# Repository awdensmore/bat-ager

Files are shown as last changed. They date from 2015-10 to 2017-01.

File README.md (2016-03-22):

# bat-ager

This project is an automated hardware and software tool for aging batteries in a precise fashion. The repo includes both hardware schematics and firmware.

**HARDWARE**

The aging process is done by repeatedly charging and discharging the battery. The hardware therefore switches between a charging mode and a discharging mode. Charging is done using a bi-directional DC/DC converter powered by a benchtop supply. Discharging is done via a DC/DC converter, carefully controlling a fet that shorts the battery to ground. Current is measured using a shunt and op-amp. The PCB is divided into five charging sections so that multiple batteries may be aged simultaneously. The system is controlled using an STM32F0 MCU. Also supports injecting a small AC ripple voltage during charging and discharging, which is used to measure the battery's impedance in real time.

**FIRMWARE**

The firmware is based on the STM HAL libraries. Features include: 
+ Independent charge/discharge settings for each battery
+ Constant current / constant voltage charging, low-voltage disconnect
+ Programmable load for discharging
+ Injection of small AC ripple voltage
+ Data collection and reporting

~~The firmware is Arduino based to make development easy (though I use the [Arduino makefile](https://github.com/sudar/Arduino-Makefile) to make customizing and automation easier in Linux). Features will include:~~
~~+ Independent charge/discharge settings for each battery~~
~~+ Serial communication via FTDI cable. With a Raspberry Pi attached, can be monitored via SSH.~~
~~+ Safeties ?!~~

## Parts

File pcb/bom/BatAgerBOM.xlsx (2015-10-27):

Bill of Materials
PCB: | Battery Ager |  |  |  | Per Unit Cost | ZAR 397.53
 |  |  |  |  | Quantity | 2
 |  |  |  |  | Components | ZAR 795.06
 |  |  |  |  | VAT @ 14% | ZAR 111.31
 |  |  |  |  | Total | ZAR 906.37
Reference | Type | Value | Package | Manufacturer | Part # | Price (ZAR) | Link | Notes
C1 | Cap | 47uF | PTH 11.2x6.3mm | Suntan | TS13D CD110X 47UF35V | 1.24 | http://www.mantech.co.za/ProductInfo.aspx?Item=72M3151
C10 | Cap | 0.1uF | 0805 | Yageo | C0805ZRY5V9BB104 | 0.28 | http://www.mantech.co.za/ProductInfo.aspx?Item=20M0861
C11 | Cap | 150uF | PTH 11.5x8mm | Rubycon | 35YXG150M 8x11.5 | 3 | http://www.mantech.co.za/ProductInfo.aspx?Item=72M4430
C12 | Cap | 150uF | PTH 11.5x8mm | Rubycon | 35YXG150M 8x11.5 | 3 | http://www.mantech.co.za/ProductInfo.aspx?Item=72M4431
C13 | Cap | 0.1uF | 0805 | Yageo | C0805ZRY5V9BB104 | 0.28 | http://www.mantech.co.za/ProductInfo.aspx?Item=20M0861
C14 | Cap | 0.1uF | 0805 | Yageo | C0805ZRY5V9BB104 | 0.28 | http://www.mantech.co.za/ProductInfo.aspx?Item=20M0861
C15 | Cap | 0.1uF | 0805 | Yageo | C0805ZRY5V9BB104 | 0.28 | http://www.mantech.co.za/ProductInfo.aspx?Item=20M0861
C16 | Cap | 0.1uF | 0805 | Yageo | C0805ZRY5V9BB104 | 0.28 | http://www.mantech.co.za/ProductInfo.aspx?Item=20M0861
C17 | Cap | 0.1uF | 0805 | Yageo | C0805ZRY5V9BB104 | 0.28 | http://www.mantech.co.za/ProductInfo.aspx?Item=20M0861
C18 | Cap | 0.1uF | 0805 | Yageo | C0805ZRY5V9BB104 | 0.28 | http://www.mantech.co.za/ProductInfo.aspx?Item=20M0861
C19 | Cap | 0.1uF | 0805 | Yageo | C0805ZRY5V9BB104 | 0.28 | http://www.mantech.co.za/ProductInfo.aspx?Item=20M0861
C2 | Cap | 47uF | PTH 11.2x6.3mm | Suntan | TS13D CD110X 47UF35V | 1.24 | http://www.mantech.co.za/ProductInfo.aspx?Item=72M3152
C20 | Cap | 0.1uF | 0805 | Yageo | C0805ZRY5V9BB104 | 0.28 | http://www.mantech.co.za/ProductInfo.aspx?Item=20M0861
C21 | Cap | 0.1uF | 0805 | Yageo | C0805ZRY5V9BB104 | 0.28 | http://www.mantech.co.za/ProductInfo.aspx?Item=20M0861
C22 | Cap | 0.1uF | 0805 | Yageo | C0805ZRY5V9BB104 | 0.28 | http://www.mantech.co.za/ProductInfo.aspx?Item=20M0861
C3 | Cap | 22pF | 0805 | Yageo | 0805CG221J500NT | 0.08 | http://www.mantech.co.za/ProductInfo.aspx?Item=35M3075
C4 | Cap | 0.1uF | 0805 | Yageo | C0805ZRY5V9BB104 | 0.28 | http://www.mantech.co.za/ProductInfo.aspx?Item=35M1227
C5 | Cap | 22pF | 0805 | Yageo | 0805CG221J500NT | 0.08 | http://www.mantech.co.za/ProductInfo.aspx?Item=35M3075
C6 | Cap | 22pF | 0805 | Yageo | 0805CG221J500NT | 0.08 | http://www.mantech.co.za/ProductInfo.aspx?Item=35M3075
C7 | Cap | 0.1uF | 0805 | Yageo | C0805ZRY5V9BB104 | 0.28 | http://www.mantech.co.za/ProductInfo.aspx?Item=20M0861
C8 | Cap | 0.1uF | 0805 | Yageo | C0805ZRY5V9BB104 | 0.28 | http://www.mantech.co.za/ProductInfo.aspx?Item=20M0861
C9 | Cap | 0.1uF | 0805 | Yageo | C0805ZRY5V9BB104 | 0.28 | http://www.mantech.co.za/ProductInfo.aspx?Item=20M0861
CON1 | Connector | ISP | PTH 2x3 100mil pitch |  |  |  |  | On hand
D1 | LED | Green | 0805 | Bright LED | BL-HX135A-TRB | 0.96 | http://www.mantech.co.za/ProductInfo.aspx?Item=12M0187
D10 | LED | Red | 0805 | Lite-On | LTST-C170EKT | 0.63 | http://www.mantech.co.za/ProductInfo.aspx?Item=35M5825
D2 | LED | Red | 0805 | Lite-On | LTST-C170EKT | 0.63 | http://www.mantech.co.za/ProductInfo.aspx?Item=35M5825
D3 | LED | Green | 0805 | Bright LED | BL-HX135A-TRB | 0.96 | http://www.mantech.co.za/ProductInfo.aspx?Item=12M0187
D4 | LED | Red | 0805 | Lite-On | LTST-C170EKT | 0.63 | http://www.mantech.co.za/ProductInfo.aspx?Item=35M5825
D5 | LED | Green | 0805 | Bright LED | BL-HX135A-TRB | 0.96 | http://www.mantech.co.za/ProductInfo.aspx?Item=12M0187
D6 | LED | Red | 0805 | Lite-On | LTST-C170EKT | 0.63 | http://www.mantech.co.za/ProductInfo.aspx?Item=35M5825
D7 | LED | Green | 0805 | Bright LED | BL-HX135A-TRB | 0.96 | http://www.mantech.co.za/ProductInfo.aspx?Item=12M0187
D8 | LED | Red | 0805 | Lite-On | LTST-C170EKT | 0.63 | http://www.mantech.co.za/ProductInfo.aspx?Item=35M5825
D9 | LED | Green | 0805 | Bright LED | BL-HX135A-TRB | 0.96 | http://www.mantech.co.za/ProductInfo.aspx?Item=12M0187
IC1 | MCU | 2560 | TQFP100 0.5mm pitch | Atmel | ATMEGA2560 | 270.97 | Farnell UK (http://export.farnell.com/webapp/wcs/stores/servlet/ProductDisplay?catalogId=15001&urlLangId=71&langId=71&productId=65349567&storeId=10152) | 11 pounds shipping from UK (phone estimate). Qty 4 sample on order directly from Atmel
P1 | Header | FTDI | PTH 1x6 100mil pitch |  |  |  |  | On hand
P10 | Header | BAT3 TERM | PTH 1x2 150mil pitch |  |  |  |  | On hand
P11 | Header | BAT4 TERM | PTH 1x2 150mil pitch |  |  |  |  | On hand
P12 | Header | BAT5 TERM | PTH 1x2 150mil pitch |  |  |  |  | On hand
P13 | Header | -15V | PTH 1 |  |  |  |  | On hand
P14 | Header | GND | PTH 1 |  |  |  |  | On hand
P15 | Header | AUX | PTH 1x6 100mil pitch |  |  |  |  | On hand
P16 | Header | Fan | PTH 1x2 150mil pitch |  |  |  |  | On hand
P2 | Header | +15V | PTH 1 |  |  |  |  | On hand
P3 | Header | BAT1 TP | PTH 1x5 100mil pitch |  |  |  |  | On hand
P4 | Header | BAT2 TP | PTH 1x5 100mil pitch |  |  |  |  | On hand
P5 | Header | BAT3 TP | PTH 1x5 100mil pitch |  |  |  |  | On hand
P6 | Header | BAT4 TP | PTH 1x5 100mil pitch |  |  |  |  | On hand
P7 | Header | BAT5 TP | PTH 1x5 100mil pitch |  |  |  |  | On hand
P8 | Header | BAT1 TERM | PTH 1x2 150mil pitch |  |  |  |  | On hand
P9 | Header | BAT2 TERM | PTH 1x2 150mil pitch |  |  |  |  | On hand
Q01 | T / FET | NFET | TO252 | IR | IRFR3607PBF | 9.78 | http://www.mantech.co.za/ProductInfo.aspx?Item=13M1648
Q02 | T / FET | Sgnl Trans | SOT23 | NXP | BC849B | 0.35 | http://www.mantech.co.za/ProductInfo.aspx?Item=35M3304
Q03 | T / FET | PFET | TO220 | IR | IRF9530N PBF | 7.05 | http://www.mantech.co.za/ProductInfo.aspx?Item=35M4416
Q04 | T / FET | NFET | TO220 | TI | CSD18536KCS | 0 | http://www.ti.com/product/csd18536kcs | On hand. Alternate part # AUIRL1404Z (IR) available from Farnell.
Q05 | T / FET | Sgnl Trans | SOT23 | NXP | BC849B | 0.35 | http://www.mantech.co.za/ProductInfo.aspx?Item=35M3304
Q06 | T / FET | Sgnl Trans | SOT23 | NXP | BC849B | 0.35 | http://www.mantech.co.za/ProductInfo.aspx?Item=35M3304
Q07 | T / FET | PFET | TO220 | IR | IRF9530N PBF | 7.05 | http://www.mantech.co.za/ProductInfo.aspx?Item=35M4416
Q08 | T / FET | NFET | TO220 | TI | CSD18536KCS | 0 | http://www.ti.com/product/csd18536kcs | On hand. Alternate part # AUIRL1404Z (IR) available from Farnell.
Q09 | T / FET | Sgnl Trans | SOT23 | NXP | BC849B | 0.35 | http://www.mantech.co.za/ProductInfo.aspx?Item=35M3304
Q10 | T / FET | Sgnl Trans | SOT23 | NXP | BC849B | 0.35 | http://www.mantech.co.za/ProductInfo.aspx?Item=35M3304
Q11 | T / FET | PFET | TO220 | IR | IRF9530N PBF | 7.05 | http://www.mantech.co.za/ProductInfo.aspx?Item=35M4416
Q12 | T / FET | Sgnl Trans | SOT23 | NXP | BC849B | 0.35 | http://www.mantech.co.za/ProductInfo.aspx?Item=35M3304
Q13 | T / FET | NFET | TO220 | TI | CSD18536KCS | 0 | http://www.ti.com/product/csd18536kcs | On hand. Alternate part # AUIRL1404Z (IR) available from Farnell.
Q14 | T / FET | Sgnl Trans | SOT23 | NXP | BC849B | 0.35 | http://www.mantech.co.za/ProductInfo.aspx?Item=35M3304
Q15 | T / FET | PFET | TO220 | IR | IRF9530N PBF | 7.05 | http://www.mantech.co.za/ProductInfo.aspx?Item=35M4416
Q16 | T / FET | Sgnl Trans | SOT23 | NXP | BC849B | 0.35 | http://www.mantech.co.za/ProductInfo.aspx?Item=35M3304
Q17 | T / FET | NFET | TO220 | TI | CSD18536KCS | 0 | http://www.ti.com/product/csd18536kcs | On hand. Alternate part # AUIRL1404Z (IR) available from Farnell.
Q18 | T / FET | Sgnl Trans | SOT23 | NXP | BC849B | 0.35 | http://www.mantech.co.za/ProductInfo.aspx?Item=35M3304
Q19 | T / FET | PFET | TO220 | IR | IRF9530N PBF | 7.05 | http://www.mantech.co.za/ProductInfo.aspx?Item=35M4416
Q20 | T / FET | Sgnl Trans | SOT23 | NXP | BC849B | 0.35 | http://www.mantech.co.za/ProductInfo.aspx?Item=35M3304
Q21 | T / FET | NFET | TO220 | TI | CSD18536KCS | 0 | http://www.ti.com/product/csd18536kcs | On hand. Alternate part # AUIRL1404Z (IR) available from Farnell.
Q22 | T / FET | NFET | TO220 | TI | IRFR3607PBF | 9.78 | http://www.mantech.co.za/ProductInfo.aspx?Item=13M1648
Q23 | T / FET | Sgnl Trans | SOT23 | NXP | BC849B | 0.35 | http://www.mantech.co.za/ProductInfo.aspx?Item=35M3304
Q24 | T / FET | Sgnl Trans | SOT23 | NXP | BC849B | 0.35 | http://www.mantech.co.za/ProductInfo.aspx?Item=35M3304
R1 | Resistor | 1k | 0805 | Yageo | RC0805JR-07 1K | 0.05 | http://www.mantech.co.za/ProductInfo.aspx?Item=35M1421
R10 | Resistor |  | PTH 10mm
R11 | Resistor |  | PTH 10mm
R12 | Resistor | 240 | 0805 | Yageo | RC0805FR-07 240R | 0.05 | http://www.mantech.co.za/ProductInfo.aspx?Item=35M3317
R13 | Resistor | 1k | 0805 | Yageo | RC0805JR-07 1K | 0.05 | http://www.mantech.co.za/ProductInfo.aspx?Item=35M1424
R14 | Resistor |  | PTH 10mm
R15 | Resistor | 1k | 0805 | Yageo | RC0805JR-07 1K | 0.05 | http://www.mantech.co.za/ProductInfo.aspx?Item=35M1425
R16 | Resistor | 1k | 0805 | Yageo | RC0805JR-07 1K | 0.05 | http://www.mantech.co.za/ProductInfo.aspx?Item=35M1426
R17 | Resistor | 240 | 0805 | Yageo | RC0805FR-07 240R | 0.05 | http://www.mantech.co.za/ProductInfo.aspx?Item=35M3317
R18 | Resistor | 240 | 0805 | Yageo | RC0805FR-07 240R | 0.05 | http://www.mantech.co.za/ProductInfo.aspx?Item=35M3317
R19 | Resistor | 0.056 | 2512 | Yageo | RL2512 FK-07 0R056 | 1.78 | http://www.mantech.co.za/ProductInfo.aspx?Item=20M0406
R2 | Resistor | 10k | 0805 | Yageo | RC0805JR-07 10K | 0.11 | http://www.mantech.co.za/ProductInfo.aspx?Item=35M1480
R20 | Resistor |  | PTH 10mm
R21 | Resistor |  | PTH 10mm
R22 | Resistor |  | PTH 10mm
R23 | Resistor |  | PTH 10mm
R24 | Resistor |  | PTH 10mm
R25 | Resistor |  | PTH 10mm
R26 | Resistor |  | PTH 10mm
R27 | Resistor | 240 | 0805 | Yageo | RC0805FR-07 240R | 0.05 | http://www.mantech.co.za/ProductInfo.aspx?Item=35M3317
R28 | Resistor | 1k | 0805 | Yageo | RC0805JR-07 1K | 0.05 | http://www.mantech.co.za/ProductInfo.aspx?Item=35M1427
R29 | Resistor |  | PTH 10mm
R3 | Resistor | 1M | 0805 | Yageo | RC0805JR-071M | 0.1 | http://www.mantech.co.za/ProductInfo.aspx?Item=35M3114
R30 | Resistor | 1k | 0805 | Yageo | RC0805JR-07 1K | 0.05 | http://www.mantech.co.za/ProductInfo.aspx?Item=35M1428
R31 | Resistor | 1k | 0805 | Yageo | RC0805JR-07 1K | 0.05 | http://www.mantech.co.za/ProductInfo.aspx?Item=35M1429
R32 | Resistor | 240 | 0805 | Yageo | RC0805FR-07 240R | 0.05 | http://www.mantech.co.za/ProductInfo.aspx?Item=35M3317
R33 | Resistor | 240 | 0805 | Yageo | RC0805FR-07 240R | 0.05 | http://www.mantech.co.za/ProductInfo.aspx?Item=35M3317
R34 | Resistor | 0.056 | 2512 | Yageo | RL2512 FK-07 0R056 | 1.78 | http://www.mantech.co.za/ProductInfo.aspx?Item=20M0406
R35 | Resistor |  | PTH 10mm
R36 | Resistor |  | PTH 10mm
R37 | Resistor |  | PTH 10mm
R38 | Resistor |  | PTH 10mm
R39 | Resistor |  | PTH 10mm
R4 | Resistor | 0 | 0805 | Yageo | RC0805JR-07 0R0 | 0.04 | http://www.mantech.co.za/ProductInfo.aspx?Item=20M0071
R40 | Resistor |  | PTH 10mm
R41 | Resistor |  | PTH 10mm
R42 | Resistor | 240 | 0805 | Yageo | RC0805FR-07 240R | 0.05 | http://www.mantech.co.za/ProductInfo.aspx?Item=35M3317
R43 | Resistor | 1k | 0805 | Yageo | RC0805JR-07 1K | 0.05 | http://www.mantech.co.za/ProductInfo.aspx?Item=35M1430
R44 | Resistor |  | PTH 10mm
R45 | Resistor | 1k | 0805 | Yageo | RC0805JR-07 1K | 0.05 | http://www.mantech.co.za/ProductInfo.aspx?Item=35M1431
R46 | Resistor | 1k | 0805 | Yageo | RC0805JR-07 1K | 0.05 | http://www.mantech.co.za/ProductInfo.aspx?Item=35M1432
R47 | Resistor | 240 | 0805 | Yageo | RC0805FR-07 240R | 0.05 | http://www.mantech.co.za/ProductInfo.aspx?Item=35M3317
R48 | Resistor | 240 | 0805 | Yageo | RC0805FR-07 240R | 0.05 | http://www.mantech.co.za/ProductInfo.aspx?Item=35M3317
R49 | Resistor | 0.056 | 2512 | Yageo | RL2512 FK-07 0R056 | 1.78 | http://www.mantech.co.za/ProductInfo.aspx?Item=20M0406
R5 | Resistor | 1k | 0805 | Yageo | RC0805JR-07 1K | 0.05 | http://www.mantech.co.za/ProductInfo.aspx?Item=35M1422
R50 | Resistor |  | PTH 10mm
R51 | Resistor |  | PTH 10mm
R52 | Resistor |  | PTH 10mm
R53 | Resistor |  | PTH 10mm
R54 | Resistor |  | PTH 10mm
R55 | Resistor |  | PTH 10mm
R56 | Resistor |  | PTH 10mm
R57 | Resistor | 240 | 0805 | Yageo | RC0805FR-07 240R | 0.05 | http://www.mantech.co.za/ProductInfo.aspx?Item=35M3317
R58 | Resistor | 1k | 0805 | Yageo | RC0805JR-07 1K | 0.05 | http://www.mantech.co.za/ProductInfo.aspx?Item=35M1433
R59 | Resistor |  | PTH 10mm
R6 | Resistor | 1k | 0805 | Yageo | RC0805JR-07 1K | 0.05 | http://www.mantech.co.za/ProductInfo.aspx?Item=35M1423
R60 | Resistor | 1k | 0805 | Yageo | RC0805JR-07 1K | 0.05 | http://www.mantech.co.za/ProductInfo.aspx?Item=35M1434
R61 | Resistor | 1k | 0805 | Yageo | RC0805JR-07 1K | 0.05 | http://www.mantech.co.za/ProductInfo.aspx?Item=35M1435
R62 | Resistor | 240 | 0805 | Yageo | RC0805FR-07 240R | 0.05 | http://www.mantech.co.za/ProductInfo.aspx?Item=35M3317
R63 | Resistor | 240 | 0805 | Yageo | RC0805FR-07 240R | 0.05 | http://www.mantech.co.za/ProductInfo.aspx?Item=35M3317
R64 | Resistor | 0.056 | 2512 | Yageo | RL2512 FK-07 0R056 | 1.78 | http://www.mantech.co.za/ProductInfo.aspx?Item=20M0406
R65 | Resistor |  | PTH 10mm
R66 | Resistor |  | PTH 10mm
R67 | Resistor |  | PTH 10mm
R68 | Resistor |  | PTH 10mm
R69 | Resistor |  | PTH 10mm
R7 | Resistor |  | PTH 10mm
R70 | Resistor |  | PTH 10mm
R71 | Resistor |  | PTH 10mm
R72 | Resistor | 240 | 0805 | Yageo | RC0805FR-07 240R | 0.05 | http://www.mantech.co.za/ProductInfo.aspx?Item=35M3317
R73 | Resistor | 1k | 0805 | Yageo | RC0805JR-07 1K | 0.05 | http://www.mantech.co.za/ProductInfo.aspx?Item=35M1436
R74 | Resistor |  | PTH 10mm
R75 | Resistor | 1k | 0805 | Yageo | RC0805JR-07 1K | 0.05 | http://www.mantech.co.za/ProductInfo.aspx?Item=35M1437
R76 | Resistor | 1k | 0805 | Yageo | RC0805JR-07 1K | 0.05 | http://www.mantech.co.za/ProductInfo.aspx?Item=35M1438
R77 | Resistor | 240 | 0805 | Yageo | RC0805FR-07 240R | 0.05 | http://www.mantech.co.za/ProductInfo.aspx?Item=35M3317
R78 | Resistor | 240 | 0805 | Yageo | RC0805FR-07 240R | 0.05 | http://www.mantech.co.za/ProductInfo.aspx?Item=35M3317
R79 | Resistor | 0.056 | 2512 | Yageo | RL2512 FK-07 0R056 | 1.78 | http://www.mantech.co.za/ProductInfo.aspx?Item=20M0406
R8 | Resistor |  | PTH 10mm
R80 | Resistor |  | PTH 10mm
R81 | Resistor |  | PTH 10mm
R82 | Resistor | 240 | 0805 | Yageo | RC0805FR-07 240R | 0.05 | http://www.mantech.co.za/ProductInfo.aspx?Item=35M3317
R83 | Resistor | 240 | 0805 | Yageo | RC0805FR-07 240R | 0.05 | http://www.mantech.co.za/ProductInfo.aspx?Item=35M3317
R84 | Resistor | 1k | 0805 | Yageo | RC0805JR-07 1K | 0.05 | http://www.mantech.co.za/ProductInfo.aspx?Item=35M1436
R9 | Resistor |  | PTH 10mm
SW1 | Switch |  | PTH 4pos | MEC | MTS-1102A TS-2 5MM | 2.97 | http://www.mantech.co.za/ProductInfo.aspx?Item=72M1360
U1 | IC | Op-amp | SOIC-8 | On-Semi | LM358DR2G DBK | 2.7 | http://www.mantech.co.za/ProductInfo.aspx?Item=72M1732
U2 | IC | Op-amp | SOIC-8 | On-Semi | LM358DR2G DBK | 3.7 | http://www.mantech.co.za/ProductInfo.aspx?Item=72M1733
U3 | IC | Op-amp | SOIC-8 | On-Semi | LM358DR2G DBK | 4.7 | http://www.mantech.co.za/ProductInfo.aspx?Item=72M1734
U4 | IC | Op-amp | SOIC-8 | On-Semi | LM358DR2G DBK | 5.7 | http://www.mantech.co.za/ProductInfo.aspx?Item=72M1735
U5 | IC | Op-amp | SOIC-8 | On-Semi | LM358DR2G DBK | 6.7 | http://www.mantech.co.za/ProductInfo.aspx?Item=72M1736
U6 | IC | Op-amp | SOIC-8 | On-Semi | LM358DR2G DBK | 7.7 | http://www.mantech.co.za/ProductInfo.aspx?Item=72M1737
Y1 | Crystal | 16MHz | HC49-USL | Mercury | 16.000MHZ-LP | 1.56 | http://www.mantech.co.za/ProductInfo.aspx?Item=65M1918-H
Other Mantech components
RJ45 |  |  |  |  | X98088S 8P8C MULTI | 7.68 | http://www.mantech.co.za/ProductInfo.aspx?Item=83M0020
14 pin DIP socket |  |  |  |  | ISS14T1/03/RH | 1.06 | http://www.mantech.co.za/ProductInfo.aspx?Item=70M0072 | MOQ: 34
8 pin DIP socket |  |  |  |  | ISS08T1/03 | 0.8 | http://www.mantech.co.za/ProductInfo.aspx?Item=70M0071 | MOQ: 60

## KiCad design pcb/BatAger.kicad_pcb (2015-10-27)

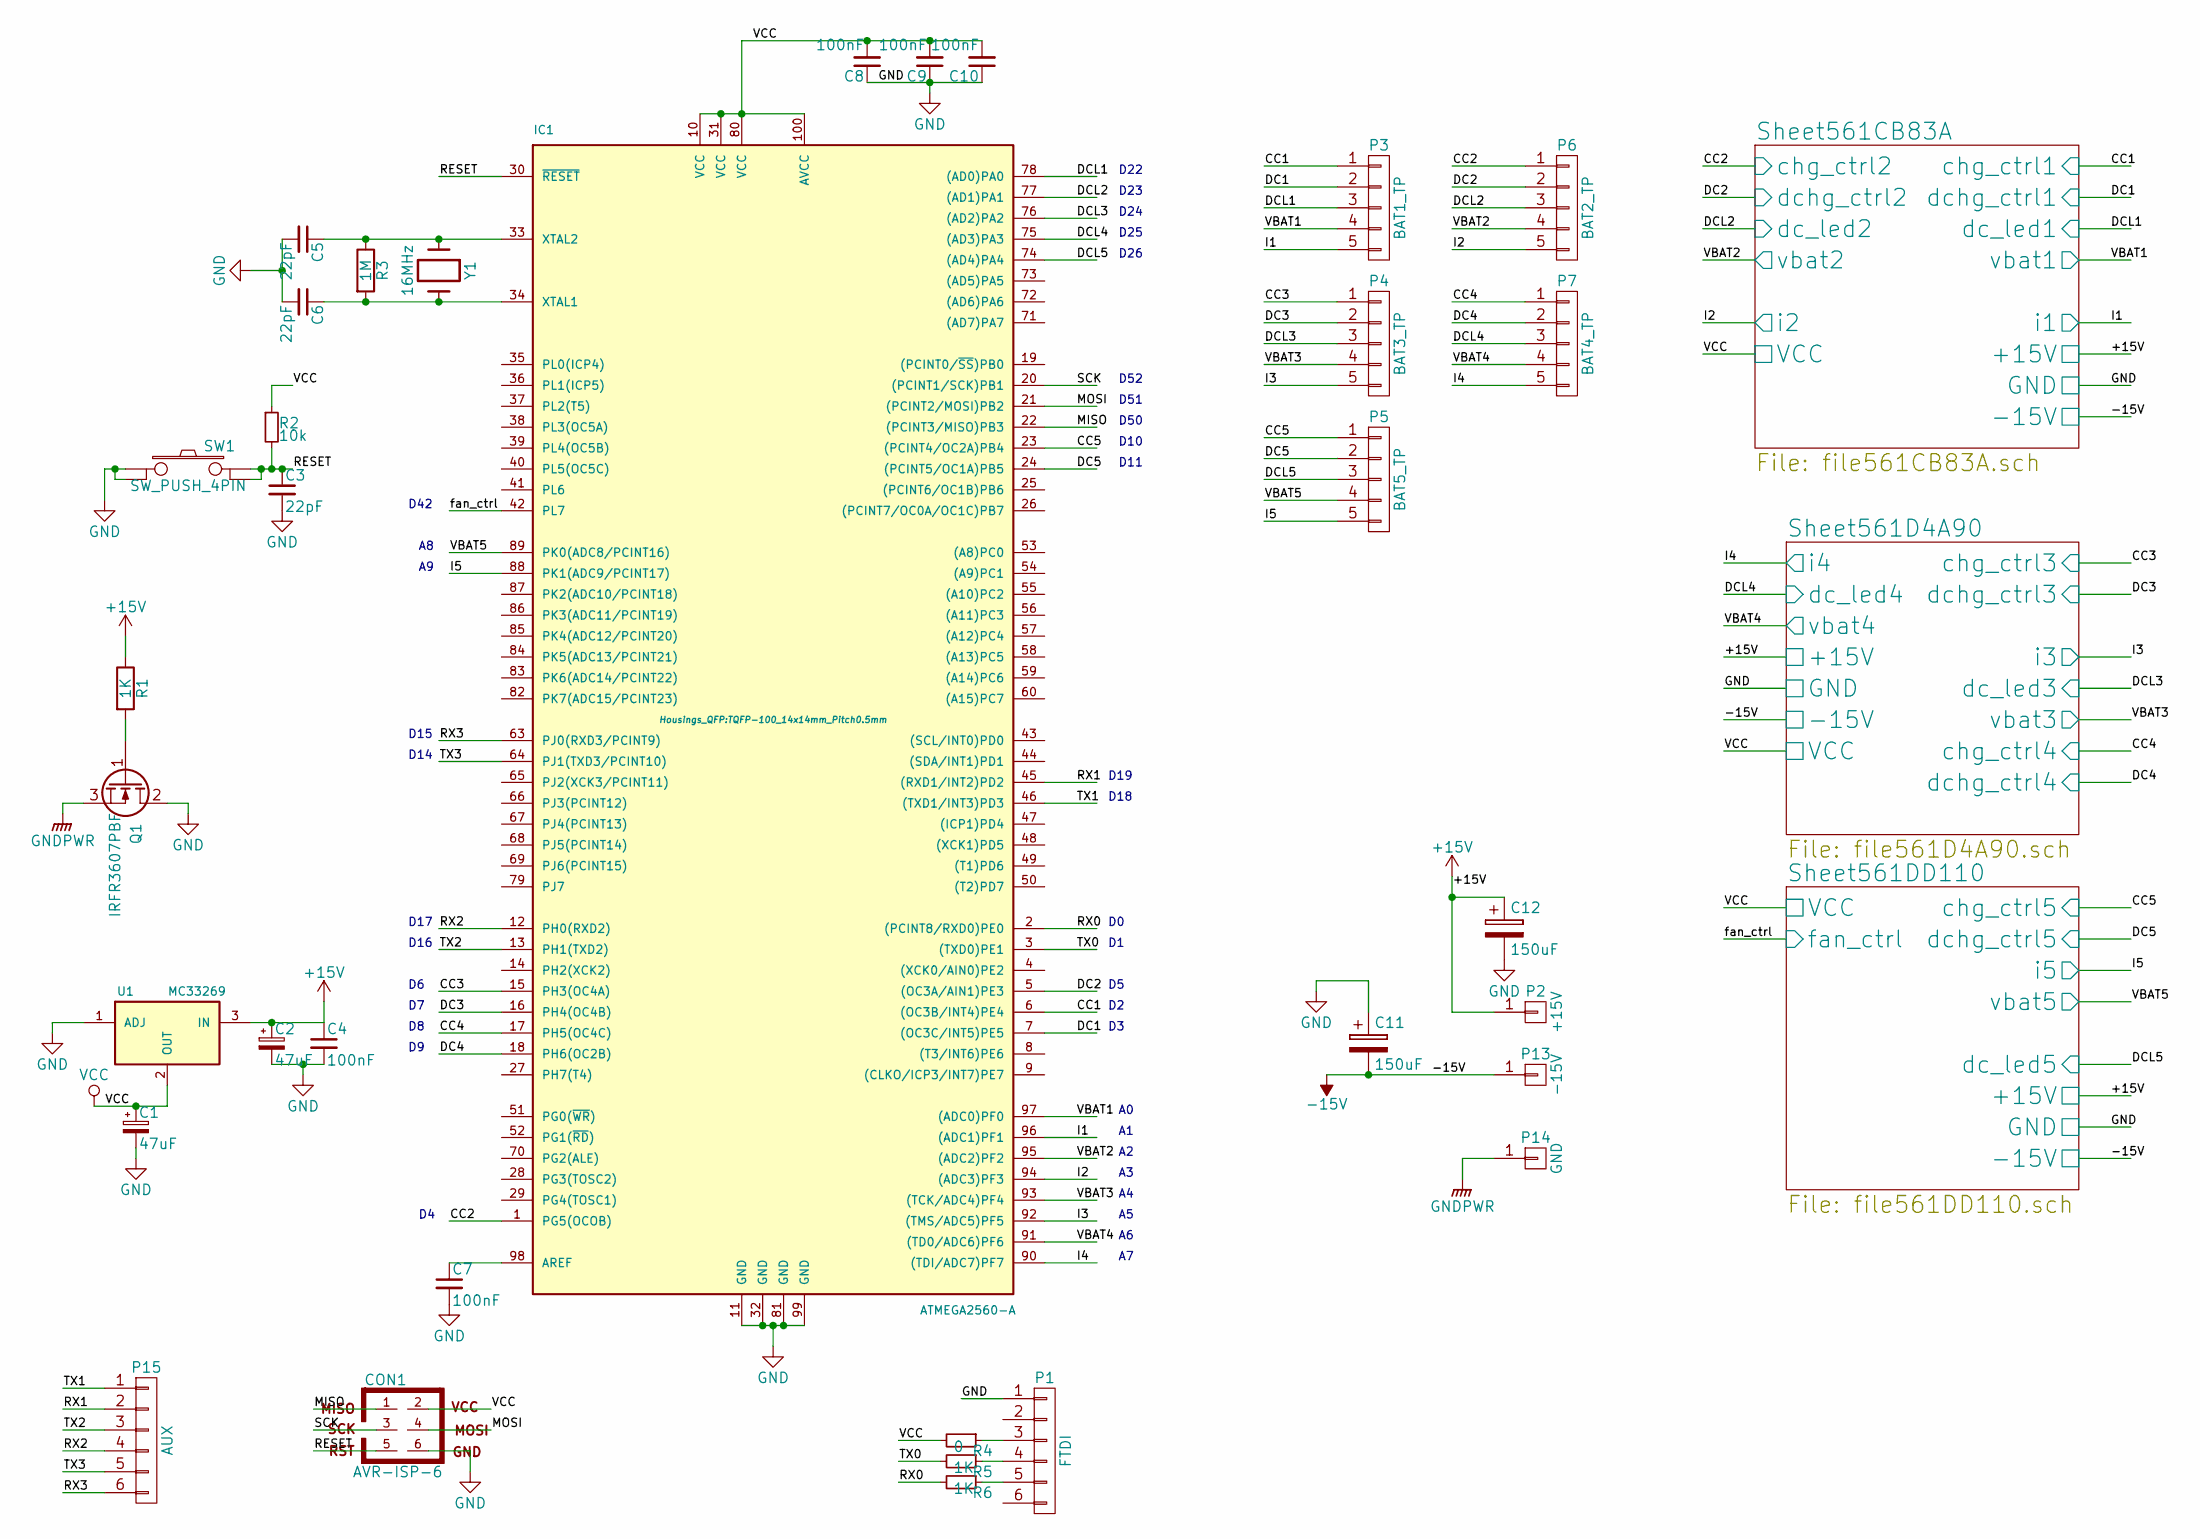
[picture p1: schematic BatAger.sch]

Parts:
C1, C2: 47uF; Elko_vert_11.2x6.3mm_RM2.5
C3, C5, C6: 22pF; C_0805_HandSoldering
C4, C7, C8, C9, C10: 100nF; C_0805_HandSoldering
C11, C12: 150uF; Elko_vert_11.5x8mm_RM3.5
CON1: AVR-ISP-6; Pin_Header_Straight_2x03
IC1: ATMEGA2560-A; TQFP-100_14x14mm_Pitch0.5mm
P1: FTDI; PINHEAD1-6
P2: +15V; Pin_Header_Straight_1x01
P3: BAT1_TP; Pin_Header_Straight_1x05
P4: BAT3_TP; Pin_Header_Straight_1x05
P5: BAT5_TP; Pin_Header_Straight_1x05
P6: BAT2_TP; Pin_Header_Straight_1x05
P7: BAT4_TP; Pin_Header_Straight_1x05
P13: -15V; Pin_Header_Straight_1x01
P14: GND; Pin_Header_Straight_1x01
P15: AUX; Pin_Header_Straight_1x06
Q1: IRFR3607PBF; TO-252-2Lead
R1, R5, R6: 1K; R_0805_HandSoldering
R2: 10k; R_0805_HandSoldering
R3: 1M; R_0805_HandSoldering
R4: 0; R_0805_HandSoldering
SW1: SW_PUSH_4PIN; SW_PUSH_4.5x6.5mm
U1: MC33269; TO-252-2Lead
Y1: 16MHz; Crystal_HC49-U_Vertical

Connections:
+15V: C2.1, C4.1, C12.1, P2.1, R1.1, U1.3 (IN); also elsewhere on the board
-15V: C11.2, P13.1; also elsewhere on the board
/MISO: CON1.1, IC1.22 ((PCINT3/MISO)PB3)
/MOSI: CON1.4, IC1.21 ((PCINT2/MOSI)PB2)
/RESET: C3.1, CON1.5, IC1.30 (~RESET), R2.2, SW1.2
/RX0: IC1.2 ((PCINT8/RXD0)PE0), R6.2
/RX1: IC1.45 ((RXD1/INT2)PD2), P15.2
/RX2: IC1.12 (PH0(RXD2)), P15.4
/RX3: IC1.63 (PJ0(RXD3/PCINT9)), P15.6
/SCK: CON1.3, IC1.20 ((PCINT1/SCK)PB1)
/Sheet561CB83A/chg_ctrl1: IC1.6 ((OC3B/INT4)PE4), P3.1; also elsewhere on the board
/Sheet561CB83A/chg_ctrl2: IC1.1 (PG5(OCOB)), P6.1; also elsewhere on the board
/Sheet561CB83A/dc_led1: IC1.78 ((AD0)PA0), P3.3; also elsewhere on the board
/Sheet561CB83A/dc_led2: IC1.77 ((AD1)PA1), P6.3; also elsewhere on the board
/Sheet561CB83A/dchg_ctrl1: IC1.7 ((OC3C/INT5)PE5), P3.2; also elsewhere on the board
/Sheet561CB83A/dchg_ctrl2: IC1.5 ((OC3A/AIN1)PE3), P6.2; also elsewhere on the board
/Sheet561CB83A/i1: IC1.96 ((ADC1)PF1), P3.5; also elsewhere on the board
/Sheet561CB83A/i2: IC1.94 ((ADC3)PF3), P6.5; also elsewhere on the board
/Sheet561CB83A/vbat1: IC1.97 ((ADC0)PF0), P3.4; also elsewhere on the board
/Sheet561CB83A/vbat2: IC1.95 ((ADC2)PF2), P6.4; also elsewhere on the board
/Sheet561D4A90/chg_ctrl3: IC1.15 (PH3(OC4A)), P4.1; also elsewhere on the board
/Sheet561D4A90/chg_ctrl4: IC1.17 (PH5(OC4C)), P7.1; also elsewhere on the board
/Sheet561D4A90/dc_led3: IC1.76 ((AD2)PA2), P4.3; also elsewhere on the board
/Sheet561D4A90/dc_led4: IC1.75 ((AD3)PA3), P7.3; also elsewhere on the board
/Sheet561D4A90/dchg_ctrl3: IC1.16 (PH4(OC4B)), P4.2; also elsewhere on the board
/Sheet561D4A90/dchg_ctrl4: IC1.18 (PH6(OC2B)), P7.2; also elsewhere on the board
/Sheet561D4A90/i3: IC1.92 ((TMS/ADC5)PF5), P4.5; also elsewhere on the board
/Sheet561D4A90/i4: IC1.90 ((TDI/ADC7)PF7), P7.5; also elsewhere on the board
/Sheet561D4A90/vbat3: IC1.93 ((TCK/ADC4)PF4), P4.4; also elsewhere on the board
/Sheet561D4A90/vbat4: IC1.91 ((TD0/ADC6)PF6), P7.4; also elsewhere on the board
/Sheet561DD110/chg_ctrl5: IC1.23 ((PCINT4/OC2A)PB4), P5.1; also elsewhere on the board
/Sheet561DD110/dc_led5: IC1.74 ((AD4)PA4), P5.3; also elsewhere on the board
/Sheet561DD110/dchg_ctrl5: IC1.24 ((PCINT5/OC1A)PB5), P5.2; also elsewhere on the board
/Sheet561DD110/fan_ctrl: IC1.42 (PL7); also elsewhere on the board
/Sheet561DD110/i5: IC1.88 (PK1(ADC9/PCINT17)), P5.5; also elsewhere on the board
/Sheet561DD110/vbat5: IC1.89 (PK0(ADC8/PCINT16)), P5.4; also elsewhere on the board
/TX0: IC1.3 ((TXD0)PE1), R5.2
/TX1: IC1.46 ((TXD1/INT3)PD3), P15.1
/TX2: IC1.13 (PH1(TXD2)), P15.3
/TX3: IC1.64 (PJ1(TXD3/PCINT10)), P15.5
GND: C1.2, C2.2, C3.2, C4.2, C5.2, C6.2, C7.2, C8.1, C9.1, C10.1, C11.1, C12.2, CON1.6, IC1.11 (GND), IC1.32 (GND), IC1.81 (GND), IC1.99 (GND), P1.1, Q1.2 (D), SW1.1, U1.1 (ADJ); also elsewhere on the board
GNDPWR: P14.1, Q1.3 (S)
unnamed: C5.1, IC1.33 (XTAL2), R3.1, Y1.1
unnamed: C6.1, IC1.34 (XTAL1), R3.2, Y1.2
unnamed: C7.1, IC1.98 (AREF)
unnamed: P1.3, R4.1
unnamed: P1.4, R5.1
unnamed: P1.5, R6.1
unnamed: Q1.1 (G), R1.2
VCC: C1.1, C8.2, C9.2, C10.2, CON1.2, IC1.10 (VCC), IC1.31 (VCC), IC1.80 (VCC), IC1.100 (AVCC), R2.1, R4.2, U1.2 (OUT); also elsewhere on the board

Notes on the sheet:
D22
D23
D24
D25
D10
D11
D26
D50
D51
D52
D18
D19
D16
D17
D14
D15
D42

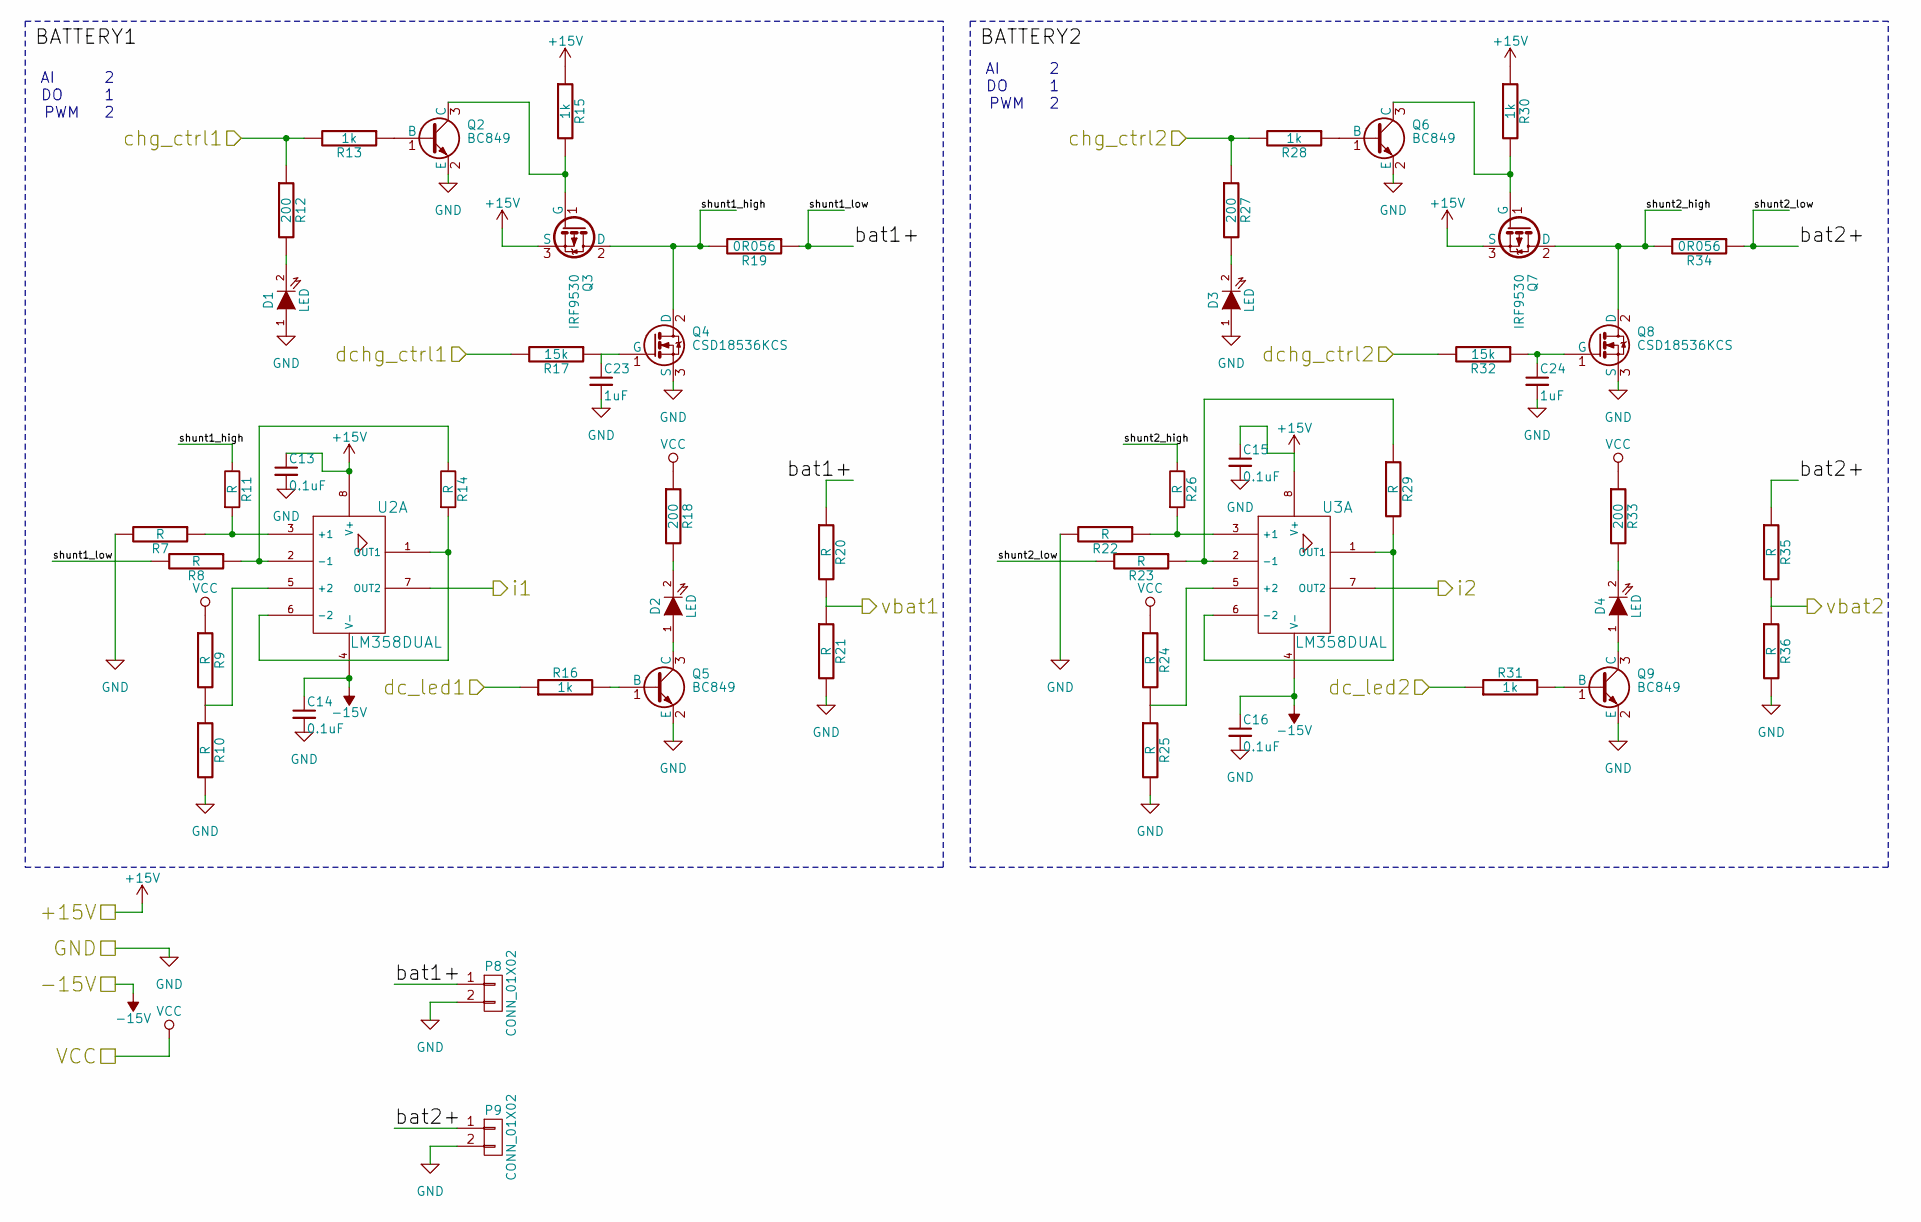
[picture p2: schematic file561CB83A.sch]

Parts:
C13, C14, C15, C16: 0.1uF; C_0805_HandSoldering
C23, C24: 1uF; C_0805_HandSoldering
D1, D2, D3, D4: LED; LED-0805
P8, P9: CONN_01X02; PINHEAD1-2_200mil
Q2, Q5, Q6, Q9: BC849; SOT-23_Handsoldering
Q3, Q7: IRF9530; TO-220
Q4, Q8: CSD18536KCS; TO-220
R7, R8, R9, R10, R11, R14, R20, R21, R22, R23, R24, R25, R26, R29, R35, R36: R; Resistor_Horizontal_RM10mm
R12, R18: 200; R_0805_HandSoldering; Part # RC0805JR-07 200R
R13, R16: 1k; R_0805_HandSoldering; Part # RC0805JR-07 200R
R15, R28, R30, R31: 1k; R_0805_HandSoldering
R17: 15k; R_0805_HandSoldering; Part # RC0805JR-07 200R
R19, R34: 0R056; R_2512_HandSoldering
R27, R33: 200; R_0805_HandSoldering
R32: 15k; R_0805_HandSoldering
U2, U3: LM358DUAL; SOIC-8_3.9x4.9mm_Pitch1.27mm

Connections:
+15V: C13.1, C15.1, Q3.3 (S), Q7.3 (S), R15.1, R30.1, U2.8 (V+), U3.8 (V+); also elsewhere on the board
-15V: C14.1, C16.1, U2.4 (V-), U3.4 (V-); also elsewhere on the board
/Sheet561CB83A/bat1+: P8.1, R8.2, R19.1, R20.1
/Sheet561CB83A/bat2+: P9.1, R23.2, R34.1, R35.1
/Sheet561CB83A/chg_ctrl1: R12.1, R13.2; also elsewhere on the board
/Sheet561CB83A/chg_ctrl2: R27.1, R28.2; also elsewhere on the board
/Sheet561CB83A/dc_led1: R16.1; also elsewhere on the board
/Sheet561CB83A/dc_led2: R31.1; also elsewhere on the board
/Sheet561CB83A/dchg_ctrl1: R17.2; also elsewhere on the board
/Sheet561CB83A/dchg_ctrl2: R32.2; also elsewhere on the board
/Sheet561CB83A/i1: U2.7 (OUT2); also elsewhere on the board
/Sheet561CB83A/i2: U3.7 (OUT2); also elsewhere on the board
/Sheet561CB83A/shunt1_high: Q3.2 (D), Q4.2 (D), R11.1, R19.2
/Sheet561CB83A/shunt2_high: Q7.2 (D), Q8.2 (D), R26.1, R34.2
/Sheet561CB83A/vbat1: R20.2, R21.1; also elsewhere on the board
/Sheet561CB83A/vbat2: R35.2, R36.1; also elsewhere on the board
GND: C13.2, C14.2, C15.2, C16.2, C23.2, C24.2, D1.1 (A), D3.1 (A), P8.2, P9.2, Q2.2 (E), Q4.3 (S), Q5.2 (E), Q6.2 (E), Q8.3 (S), Q9.2 (E), R7.2, R10.2, R21.2, R22.2, R25.2, R36.2; also elsewhere on the board
unnamed: C23.1, Q4.1 (G), R17.1
unnamed: C24.1, Q8.1 (G), R32.1
unnamed: D1.2 (K), R12.2
unnamed: D2.1 (A), Q5.3 (C)
unnamed: D2.2 (K), R18.2
unnamed: D3.2 (K), R27.2
unnamed: D4.1 (A), Q9.3 (C)
unnamed: D4.2 (K), R33.2
unnamed: Q2.1 (B), R13.1
unnamed: Q2.3 (C), Q3.1 (G), R15.2
unnamed: Q5.1 (B), R16.2
unnamed: Q6.1 (B), R28.1
unnamed: Q6.3 (C), Q7.1 (G), R30.2
unnamed: Q9.1 (B), R31.2
unnamed: R9.2, R10.1, U2.5 (+2)
unnamed: R7.1, R11.2, U2.3 (+1)
unnamed: R8.1, R14.1, U2.2 (-1)
unnamed: R14.2, U2.1 (OUT1), U2.6 (-2)
unnamed: R22.1, R26.2, U3.3 (+1)
unnamed: R23.1, R29.1, U3.2 (-1)
unnamed: R24.2, R25.1, U3.5 (+2)
unnamed: R29.2, U3.1 (OUT1), U3.6 (-2)
VCC: R9.1, R18.1, R24.1, R33.1; also elsewhere on the board

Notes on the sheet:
AI 2 DO 1 PWM 2

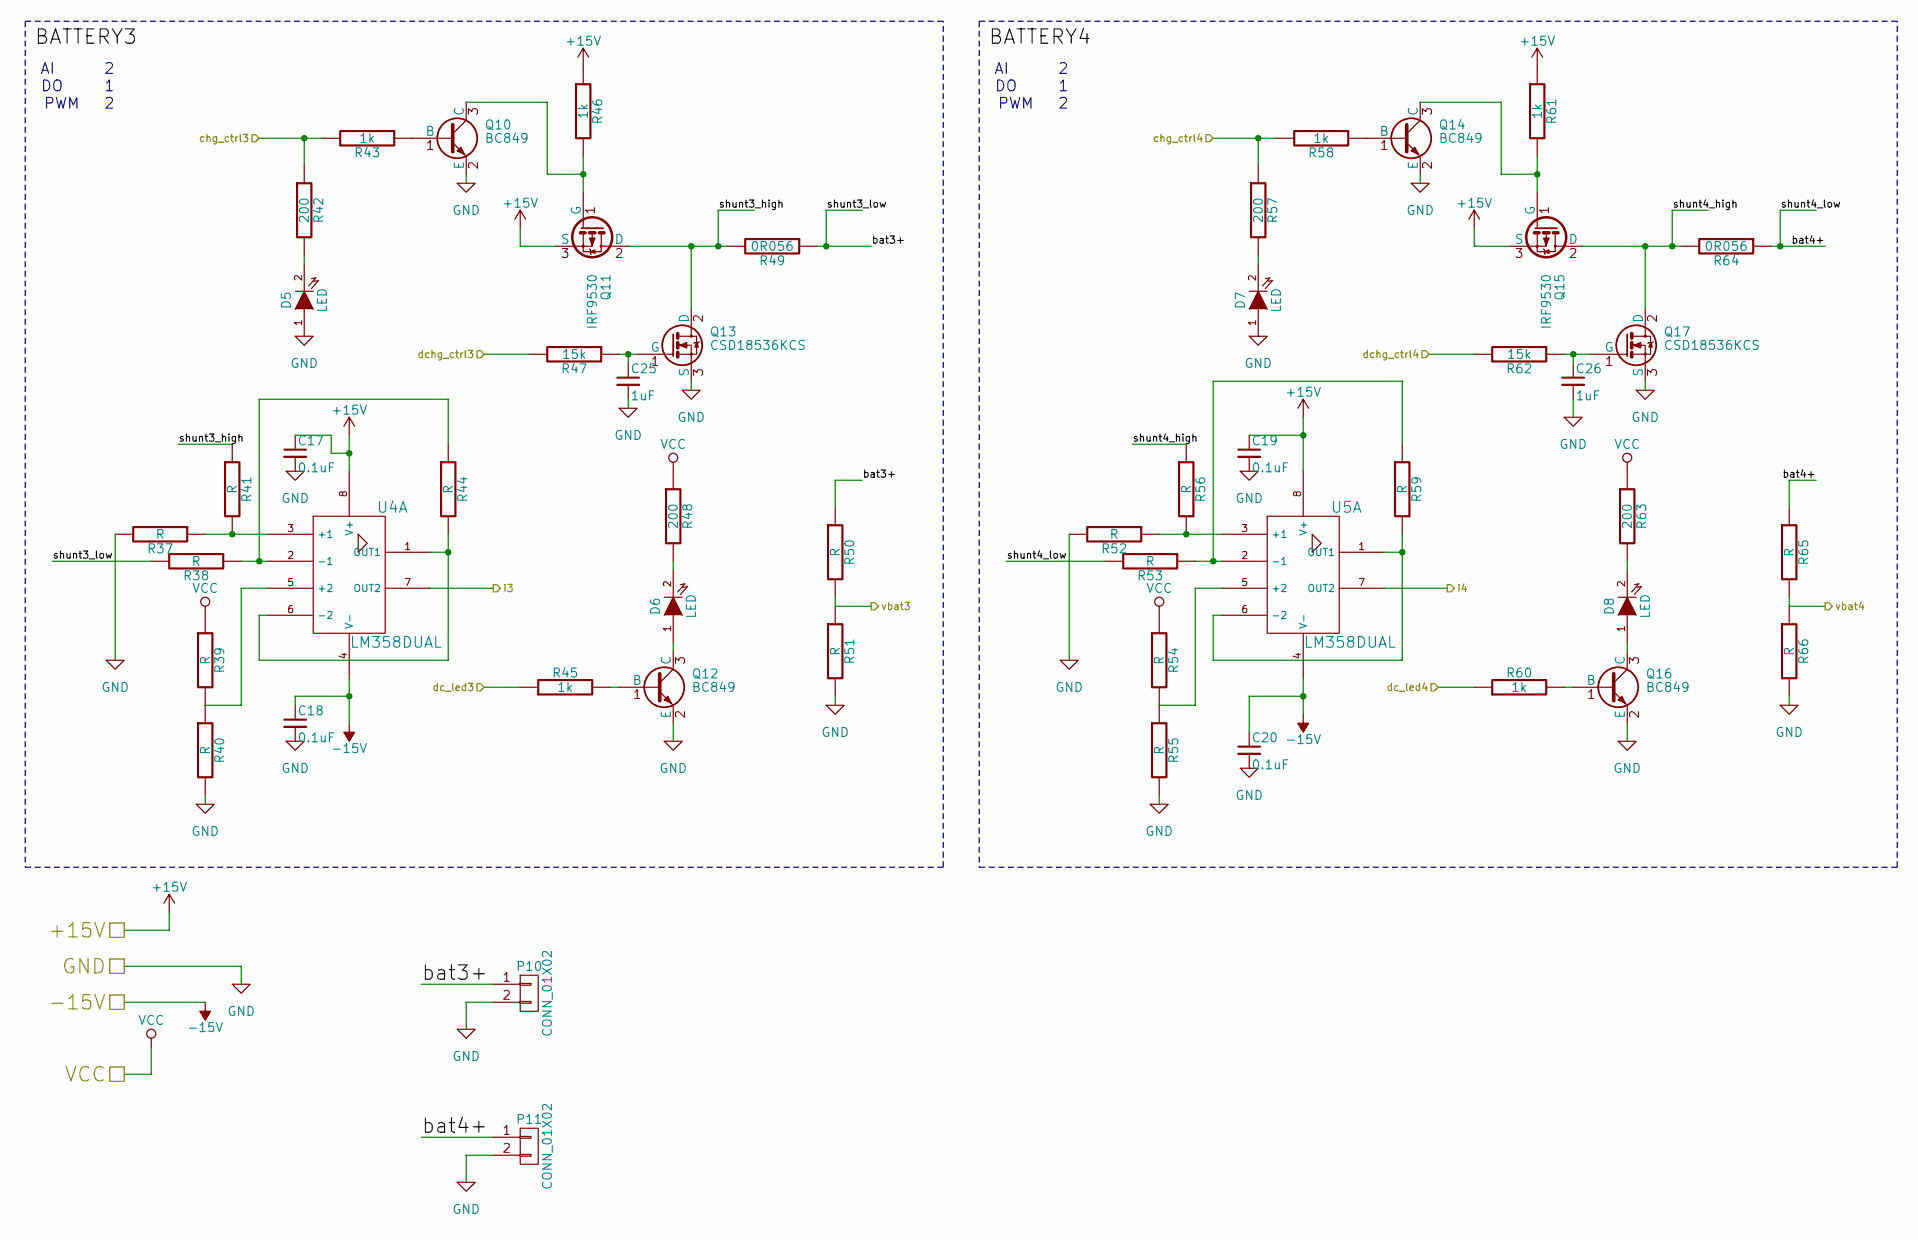
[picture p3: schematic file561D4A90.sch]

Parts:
C17, C18, C19, C20: 0.1uF; C_0805_HandSoldering
C25: 1uF; C_0805_HandSoldering
C26: 1uF; C_Disc_D3_P2.5
D5, D6, D7, D8: LED; LED-0805
P10, P11: CONN_01X02; PINHEAD1-2_200mil
Q10, Q12, Q14, Q16: BC849; SOT-23_Handsoldering
Q11, Q15: IRF9530; TO-220
Q13, Q17: CSD18536KCS; TO-220
R37, R38, R39, R40, R41, R44, R50, R51, R52, R53, R54, R55, R56, R59, R65, R66: R; Resistor_Horizontal_RM10mm
R42, R48, R57, R63: 200; R_0805_HandSoldering
R43, R45, R46, R58, R60, R61: 1k; R_0805_HandSoldering
R47: 15k; R_0805_HandSoldering
R49, R64: 0R056; R_2512_HandSoldering; Part # RL2512 FK-07 0R056
R62: 15k; Resistor_Horizontal_RM10mm
U4, U5: LM358DUAL; SOIC-8_3.9x4.9mm_Pitch1.27mm

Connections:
+15V: C17.1, C19.1, Q11.3 (S), Q15.3 (S), R46.1, R61.1, U4.8 (V+), U5.8 (V+); also elsewhere on the board
-15V: C18.1, C20.1, U4.4 (V-), U5.4 (V-); also elsewhere on the board
/Sheet561D4A90/bat3+: P10.1, R38.2, R49.1, R50.1
/Sheet561D4A90/bat4+: P11.1, R53.2, R64.1, R65.1
/Sheet561D4A90/chg_ctrl3: R42.1, R43.2; also elsewhere on the board
/Sheet561D4A90/chg_ctrl4: R57.1, R58.2; also elsewhere on the board
/Sheet561D4A90/dc_led3: R45.1; also elsewhere on the board
/Sheet561D4A90/dc_led4: R60.1; also elsewhere on the board
/Sheet561D4A90/dchg_ctrl3: R47.2; also elsewhere on the board
/Sheet561D4A90/dchg_ctrl4: R62.2; also elsewhere on the board
/Sheet561D4A90/i3: U4.7 (OUT2); also elsewhere on the board
/Sheet561D4A90/i4: U5.7 (OUT2); also elsewhere on the board
/Sheet561D4A90/shunt3_high: Q11.2 (D), Q13.2 (D), R41.1, R49.2
/Sheet561D4A90/shunt4_high: Q15.2 (D), Q17.2 (D), R56.1, R64.2
/Sheet561D4A90/vbat3: R50.2, R51.1; also elsewhere on the board
/Sheet561D4A90/vbat4: R65.2, R66.1; also elsewhere on the board
GND: C17.2, C18.2, C19.2, C20.2, C25.2, C26.2, D5.1 (A), D7.1 (A), P10.2, P11.2, Q10.2 (E), Q12.2 (E), Q13.3 (S), Q14.2 (E), Q16.2 (E), Q17.3 (S), R37.2, R40.2, R51.2, R52.2, R55.2, R66.2; also elsewhere on the board
unnamed: C25.1, Q13.1 (G), R47.1
unnamed: C26.1, Q17.1 (G), R62.1
unnamed: D5.2 (K), R42.2
unnamed: D6.1 (A), Q12.3 (C)
unnamed: D6.2 (K), R48.2
unnamed: D7.2 (K), R57.2
unnamed: D8.1 (A), Q16.3 (C)
unnamed: D8.2 (K), R63.2
unnamed: Q10.1 (B), R43.1
unnamed: Q10.3 (C), Q11.1 (G), R46.2
unnamed: Q12.1 (B), R45.2
unnamed: Q14.1 (B), R58.1
unnamed: Q14.3 (C), Q15.1 (G), R61.2
unnamed: Q16.1 (B), R60.2
unnamed: R37.1, R41.2, U4.3 (+1)
unnamed: R38.1, R44.1, U4.2 (-1)
unnamed: R39.2, R40.1, U4.5 (+2)
unnamed: R44.2, U4.1 (OUT1), U4.6 (-2)
unnamed: R52.1, R56.2, U5.3 (+1)
unnamed: R53.1, R59.1, U5.2 (-1)
unnamed: R54.2, R55.1, U5.5 (+2)
unnamed: R59.2, U5.1 (OUT1), U5.6 (-2)
VCC: R39.1, R48.1, R54.1, R63.1; also elsewhere on the board

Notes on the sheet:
AI 2 DO 1 PWM 2

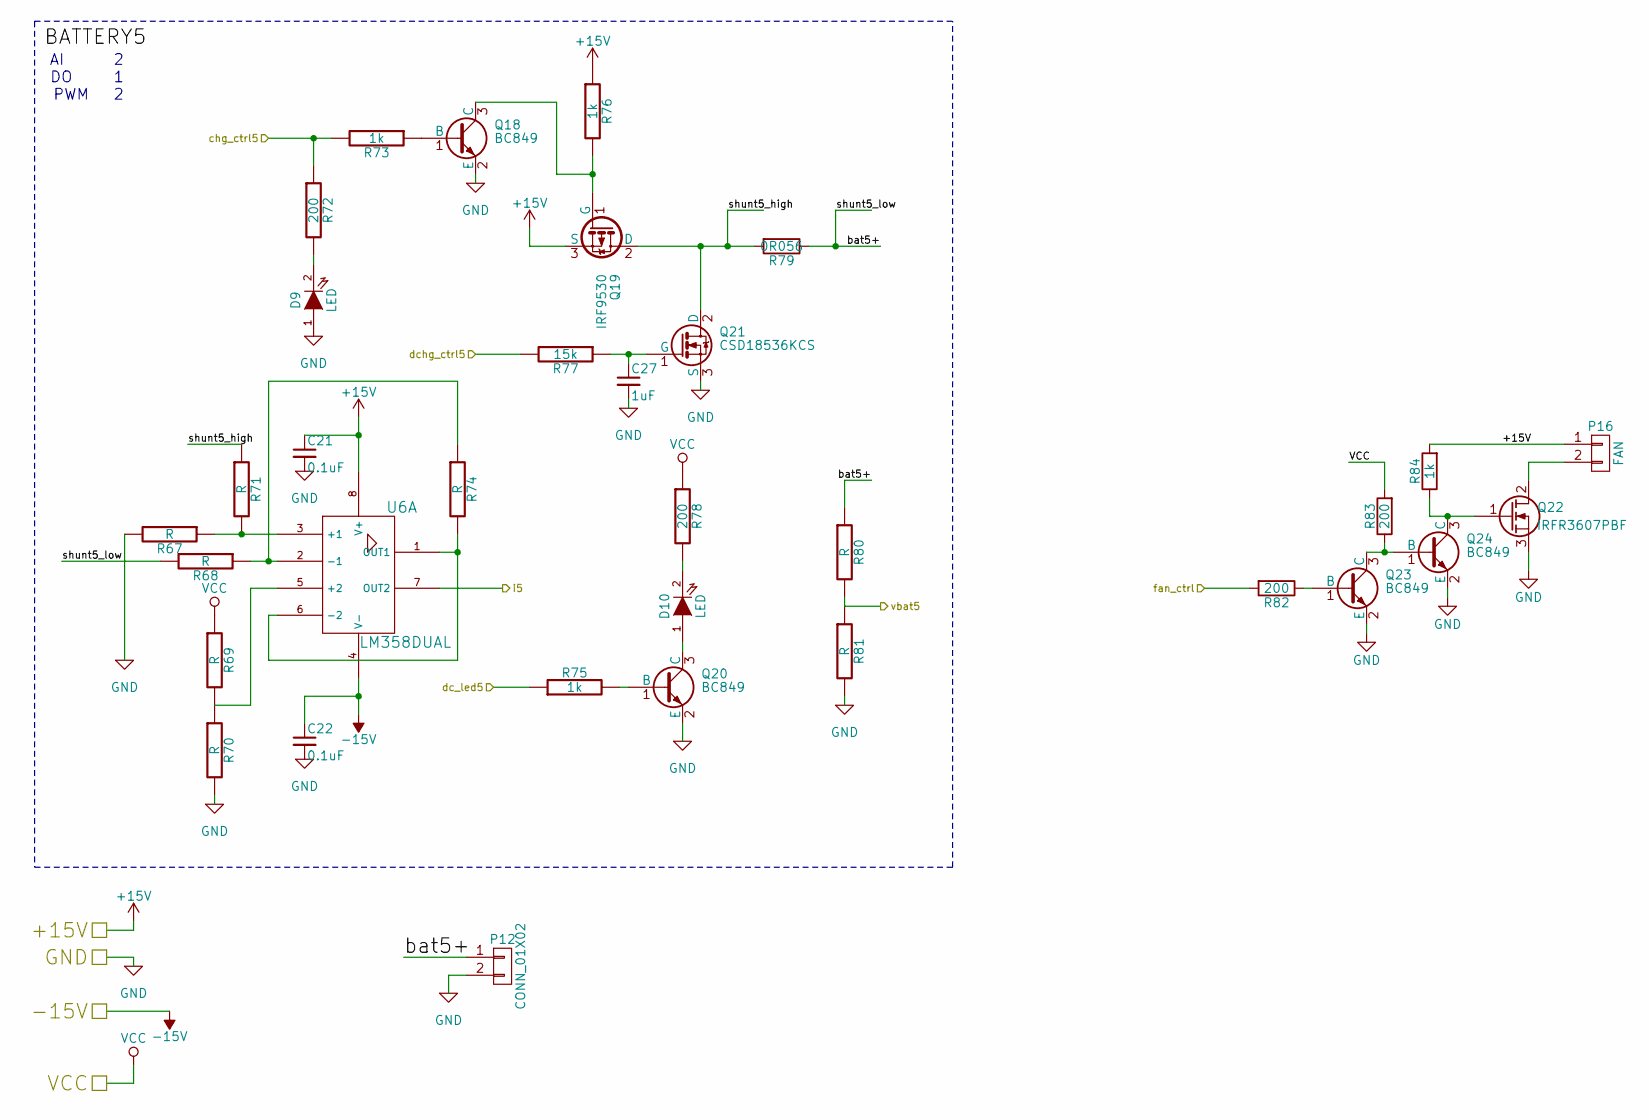
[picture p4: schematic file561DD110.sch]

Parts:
C21, C22: 0.1uF; C_0805_HandSoldering
C27: 1uF; C_0805_HandSoldering
D9, D10: LED; LED-0805
P12: CONN_01X02; PINHEAD1-2_200mil
P16: FAN; Pin_Header_Straight_1x02
Q18, Q20, Q23, Q24: BC849; SOT-23_Handsoldering
Q19: IRF9530; TO-220
Q21: CSD18536KCS; TO-220
Q22: IRFR3607PBF; TO-252-2Lead
R67, R68, R69, R70, R71, R74, R80, R81: R; Resistor_Horizontal_RM10mm
R72, R78, R82, R83: 200; R_0805_HandSoldering
R73, R75, R76, R84: 1k; R_0805_HandSoldering
R77: 15k; R_0805_HandSoldering
R79: 0R056; R_2512_HandSoldering; Part # RL2512 FK-07 0R056
U6: LM358DUAL; SOIC-8_3.9x4.9mm_Pitch1.27mm

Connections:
+15V: C21.1, P16.1, Q19.3 (S), R76.1, R84.2, U6.8 (V+); also elsewhere on the board
-15V: C22.1, U6.4 (V-); also elsewhere on the board
/Sheet561DD110/bat5+: P12.1, R68.2, R79.1, R80.1
/Sheet561DD110/chg_ctrl5: R72.1, R73.2; also elsewhere on the board
/Sheet561DD110/dc_led5: R75.1; also elsewhere on the board
/Sheet561DD110/dchg_ctrl5: R77.2; also elsewhere on the board
/Sheet561DD110/fan_ctrl: R82.2; also elsewhere on the board
/Sheet561DD110/i5: U6.7 (OUT2); also elsewhere on the board
/Sheet561DD110/shunt5_high: Q19.2 (D), Q21.2 (D), R71.1, R79.2
/Sheet561DD110/vbat5: R80.2, R81.1; also elsewhere on the board
GND: C21.2, C22.2, C27.2, D9.1 (A), P12.2, Q18.2 (E), Q20.2 (E), Q21.3 (S), Q22.3 (S), Q23.2 (E), Q24.2 (E), R67.2, R70.2, R81.2; also elsewhere on the board
unnamed: C27.1, Q21.1 (G), R77.1
unnamed: D9.2 (K), R72.2
unnamed: D10.1 (A), Q20.3 (C)
unnamed: D10.2 (K), R78.2
unnamed: P16.2, Q22.2 (D)
unnamed: Q18.1 (B), R73.1
unnamed: Q18.3 (C), Q19.1 (G), R76.2
unnamed: Q20.1 (B), R75.2
unnamed: Q22.1 (G), Q24.3 (C), R84.1
unnamed: Q23.1 (B), R82.1
unnamed: Q23.3 (C), Q24.1 (B), R83.1
unnamed: R67.1, R71.2, U6.3 (+1)
unnamed: R68.1, R74.1, U6.2 (-1)
unnamed: R69.2, R70.1, U6.5 (+2)
unnamed: R74.2, U6.1 (OUT1), U6.6 (-2)
VCC: R69.1, R78.1, R83.2; also elsewhere on the board

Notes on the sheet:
AI 2 DO 1 PWM 2

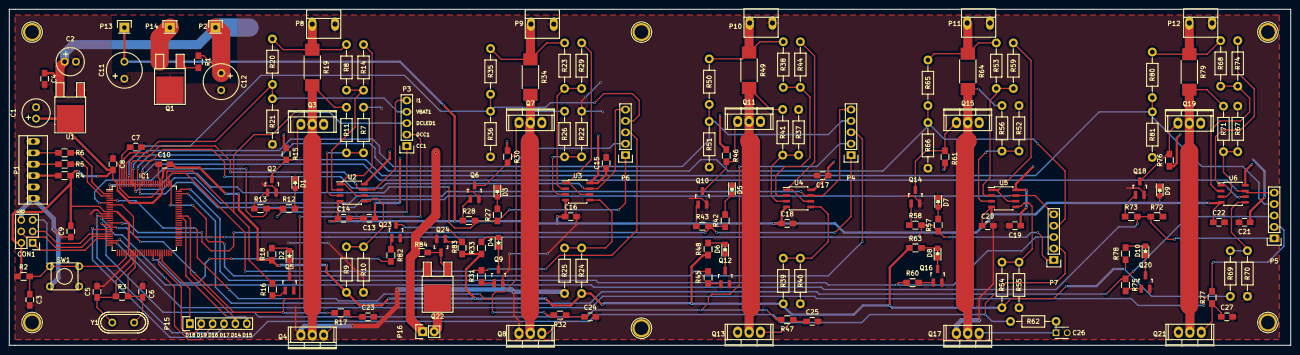
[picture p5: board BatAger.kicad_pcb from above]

Board: 2 copper layers, 285.8 x 74.9 mm, 171 parts (0 on the bottom side), 119 nets.

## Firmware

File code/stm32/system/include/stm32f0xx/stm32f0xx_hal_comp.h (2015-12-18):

/**
  ******************************************************************************
  * @file    stm32f0xx_hal_comp.h
  * @author  MCD Application Team
  * @version V1.3.0
  * @date    26-June-2015
  * @brief   Header file of COMP HAL module.
  ******************************************************************************
  * @attention
  *
  * <h2><center>&copy; COPYRIGHT(c) 2015 STMicroelectronics</center></h2>
  *
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
  ******************************************************************************  
  */

/* Define to prevent recursive inclusion -------------------------------------*/
#ifndef __STM32F0xx_HAL_COMP_H
#define __STM32F0xx_HAL_COMP_H

#ifdef __cplusplus
 extern "C" {
#endif

#if defined(STM32F051x8) || defined(STM32F058xx) || \
    defined(STM32F071xB) || defined(STM32F072xB) || defined(STM32F078xx) || \
    defined(STM32F091xC) || defined(STM32F098xx)

/* Includes ------------------------------------------------------------------*/
#include "stm32f0xx_hal_def.h"

/** @addtogroup STM32F0xx_HAL_Driver
  * @{
  */

/** @addtogroup COMP COMP
  * @{
  */ 

/* Exported types ------------------------------------------------------------*/ 
/** @defgroup COMP_Exported_Types COMP Exported Types
  * @{
  */
    
/** 
  * @brief  COMP Init structure definition  
  */ 
typedef struct
{

  uint32_t InvertingInput;     /*!< Selects the inverting input of the comparator.
                                    This parameter can be a value of @ref COMP_InvertingInput */

  uint32_t NonInvertingInput;  /*!< Selects the non inverting input of the comparator.
                                    This parameter can be a value of @ref COMP_NonInvertingInput */

  uint32_t Output;             /*!< Selects the output redirection of the comparator.
                                    This parameter can be a value of @ref COMP_Output */

  uint32_t OutputPol;          /*!< Selects the output polarity of the comparator.
                                    This parameter can be a value of @ref COMP_OutputPolarity */

  uint32_t Hysteresis;         /*!< Selects the hysteresis voltage of the comparator.
                                    This parameter can be a value of @ref COMP_Hysteresis */

  uint32_t Mode;               /*!< Selects the operating comsumption mode of the comparator
                                    to adjust the speed/consumption.
                                    This parameter can be a value of @ref COMP_Mode */

  uint32_t WindowMode;         /*!< Selects the window mode of the comparator 1 & 2.
                                    This parameter can be a value of @ref COMP_WindowMode */
  
  uint32_t TriggerMode;        /*!< Selects the trigger mode of the comparator (interrupt mode).
                                    This parameter can be a value of @ref COMP_TriggerMode */

}COMP_InitTypeDef;

/** 
  * @brief  COMP Handle Structure definition  
  */ 
typedef struct
{
  COMP_TypeDef                *Instance; /*!< Register base address    */
  COMP_InitTypeDef            Init;      /*!< COMP required parameters */
  HAL_LockTypeDef             Lock;      /*!< Locking object           */
  __IO uint32_t               State;     /*!< COMP communication state 
                                              This parameter can be a value of @ref COMP_State  */
}COMP_HandleTypeDef;

/**
  * @}
  */
  
/* Exported constants --------------------------------------------------------*/
/** @defgroup COMP_Exported_Constants COMP Exported Constants
  * @{
  */

/** @defgroup COMP_State COMP State
  * @{
  */
#define HAL_COMP_STATE_RESET             ((uint32_t)0x00000000)    /*!< COMP not yet initialized or disabled             */
#define HAL_COMP_STATE_READY             ((uint32_t)0x00000001)    /*!< COMP initialized and ready for use               */
#define HAL_COMP_STATE_READY_LOCKED      ((uint32_t)0x00000011)    /*!< COMP initialized but the configuration is locked */
#define HAL_COMP_STATE_BUSY              ((uint32_t)0x00000002)    /*!< COMP is running                                  */
#define HAL_COMP_STATE_BUSY_LOCKED       ((uint32_t)0x00000012)    /*!< COMP is running and the configuration is locked  */
/**
  * @}
  */

/** @defgroup COMP_OutputPolarity COMP OutputPolarity
  * @{
  */
#define COMP_OUTPUTPOL_NONINVERTED             ((uint32_t)0x00000000)  /*!< COMP output on GPIO isn't inverted */
#define COMP_OUTPUTPOL_INVERTED                COMP_CSR_COMP1POL       /*!< COMP output on GPIO is inverted  */
/**
  * @}
  */ 

/** @defgroup COMP_Hysteresis COMP Hysteresis
  * @{
  */
#define COMP_HYSTERESIS_NONE                   ((uint32_t)0x00000000)  /*!< No hysteresis */
#define COMP_HYSTERESIS_LOW                    COMP_CSR_COMP1HYST_0    /*!< Hysteresis level low */
#define COMP_HYSTERESIS_MEDIUM                 COMP_CSR_COMP1HYST_1    /*!< Hysteresis level medium */
#define COMP_HYSTERESIS_HIGH                   COMP_CSR_COMP1HYST      /*!< Hysteresis level high */
/**
  * @}
  */

/** @defgroup COMP_Mode COMP Mode
  * @{
  */
/* Please refer to the electrical characteristics in the device datasheet for
   the power consumption values */
#define COMP_MODE_HIGHSPEED                    ((uint32_t)0x00000000) /*!< High Speed */
#define COMP_MODE_MEDIUMSPEED                  COMP_CSR_COMP1MODE_0   /*!< Medium Speed */
#define COMP_MODE_LOWPOWER                     COMP_CSR_COMP1MODE_1   /*!< Low power mode */
#define COMP_MODE_ULTRALOWPOWER                COMP_CSR_COMP1MODE     /*!< Ultra-low power mode */
/**
  * @}
  */

/** @defgroup COMP_InvertingInput COMP InvertingInput
  * @{
  */

#define COMP_INVERTINGINPUT_1_4VREFINT         ((uint32_t)0x00000000) /*!< 1/4 VREFINT connected to comparator inverting input */
#define COMP_INVERTINGINPUT_1_2VREFINT         COMP_CSR_COMP1INSEL_0                         /*!< 1/2 VREFINT connected to comparator inverting input    */
#define COMP_INVERTINGINPUT_3_4VREFINT         COMP_CSR_COMP1INSEL_1                         /*!< 3/4 VREFINT connected to comparator inverting input    */
#define COMP_INVERTINGINPUT_VREFINT            (COMP_CSR_COMP1INSEL_1|COMP_CSR_COMP1INSEL_0) /*!< VREFINT connected to comparator inverting input        */
#define COMP_INVERTINGINPUT_DAC1               COMP_CSR_COMP1INSEL_2                         /*!< DAC_OUT1 (PA4) connected to comparator inverting input */
#define COMP_INVERTINGINPUT_DAC1SWITCHCLOSED   (COMP_CSR_COMP1INSEL_2|COMP_CSR_COMP1SW1)     /*!< DAC_OUT1 (PA4) connected to comparator inverting input 
                                                                                                  and close switch (PA0 for COMP1 only) */
#define COMP_INVERTINGINPUT_DAC2               (COMP_CSR_COMP1INSEL_2|COMP_CSR_COMP1INSEL_0) /*!< DAC_OUT2 (PA5) connected to comparator inverting input */
#define COMP_INVERTINGINPUT_IO1                (COMP_CSR_COMP1INSEL_2|COMP_CSR_COMP1INSEL_1) /*!< IO (PA0 for COMP1 and PA2 for COMP2) connected to comparator inverting input */
/**
  * @}
  */ 

/** @defgroup COMP_NonInvertingInput COMP NonInvertingInput
  * @{
  */
#define COMP_NONINVERTINGINPUT_IO1               ((uint32_t)0x00000000) /*!< I/O1 (PA1 for COMP1, PA3 for COMP2) 
                                                                             connected to comparator non inverting input */
#define COMP_NONINVERTINGINPUT_DAC1SWITCHCLOSED  COMP_CSR_COMP1SW1  /*!< DAC ouput connected to comparator COMP1 non inverting input */
/**
  * @}
  */

/** @defgroup COMP_Output COMP Output
  * @{
  */

/* Output Redirection common for COMP1 and COMP2 */
#define COMP_OUTPUT_NONE                       ((uint32_t)0x00000000)                          /*!< COMP output isn't connected to other peripherals */
#define COMP_OUTPUT_TIM1BKIN                   COMP_CSR_COMP1OUTSEL_0                          /*!< COMP output connected to TIM1 Break Input (BKIN) */
#define COMP_OUTPUT_TIM1IC1                    COMP_CSR_COMP1OUTSEL_1                          /*!< COMP output connected to TIM1 Input Capture 1 */
#define COMP_OUTPUT_TIM1OCREFCLR               (COMP_CSR_COMP1OUTSEL_1|COMP_CSR_COMP1OUTSEL_0) /*!< COMP output connected to TIM1 OCREF Clear */
#define COMP_OUTPUT_TIM2IC4                    COMP_CSR_COMP1OUTSEL_2                          /*!< COMP output connected to TIM2 Input Capture 4 */
#define COMP_OUTPUT_TIM2OCREFCLR               (COMP_CSR_COMP1OUTSEL_2|COMP_CSR_COMP1OUTSEL_0) /*!< COMP output connected to TIM2 OCREF Clear */
#define COMP_OUTPUT_TIM3IC1                    (COMP_CSR_COMP1OUTSEL_2|COMP_CSR_COMP1OUTSEL_1) /*!< COMP output connected to TIM3 Input Capture 1 */
#define COMP_OUTPUT_TIM3OCREFCLR               COMP_CSR_COMP1OUTSEL                            /*!< COMP output connected to TIM3 OCREF Clear */
/**
  * @}
  */ 

/** @defgroup COMP_OutputLevel COMP OutputLevel
  * @{
  */ 
/* When output polarity is not inverted, comparator output is low when
   the non-inverting input is at a lower voltage than the inverting input*/
#define COMP_OUTPUTLEVEL_LOW                   ((uint32_t)0x00000000)
/* When output polarity is not inverted, comparator output is high when
   the non-inverting input is at a higher voltage than the inverting input */
#define COMP_OUTPUTLEVEL_HIGH                  COMP_CSR_COMP1OUT
/**
  * @}
  */ 

/** @defgroup COMP_TriggerMode COMP TriggerMode
  * @{
  */
#define COMP_TRIGGERMODE_NONE                  ((uint32_t)0x00000000)  /*!< No External Interrupt trigger detection */
#define COMP_TRIGGERMODE_IT_RISING             ((uint32_t)0x00000001)  /*!< External Interrupt Mode with Rising edge trigger detection */
#define COMP_TRIGGERMODE_IT_FALLING            ((uint32_t)0x00000002)  /*!< External Interrupt Mode with Falling edge trigger detection */
#define COMP_TRIGGERMODE_IT_RISING_FALLING     ((uint32_t)0x00000003)  /*!< External Interrupt Mode with Rising/Falling edge trigger detection */
#define COMP_TRIGGERMODE_EVENT_RISING          ((uint32_t)0x00000010)  /*!< Event Mode with Rising edge trigger detection */
#define COMP_TRIGGERMODE_EVENT_FALLING         ((uint32_t)0x00000020)  /*!< Event Mode with Falling edge trigger detection */
#define COMP_TRIGGERMODE_EVENT_RISING_FALLING  ((uint32_t)0x00000030)  /*!< Event Mode with Rising/Falling edge trigger detection */
/**
  * @}
  */ 

/** @defgroup COMP_WindowMode COMP WindowMode
  * @{
  */
#define COMP_WINDOWMODE_DISABLE                ((uint32_t)0x00000000)  /*!< Window mode disabled */
#define COMP_WINDOWMODE_ENABLE                 COMP_CSR_WNDWEN         /*!< Window mode enabled: non inverting input of comparator 2
                                                                            is connected to the non inverting input of comparator 1 (PA1) */
/**
  * @}
  */

/** @defgroup COMP_Flag COMP Flag
  * @{
  */
#define COMP_FLAG_LOCK                         ((uint32_t)COMP_CSR_COMPxLOCK)  /*!< Lock flag */

/**
  * @}
  */

/**
  * @}
  */ 
  
/* Exported macros -----------------------------------------------------------*/
/** @defgroup COMP_Exported_Macros COMP Exported Macros
  * @{
  */

/** @brief  Reset COMP handle state
  * @param  __HANDLE__: COMP handle.
  * @retval None
  */
#define __HAL_COMP_RESET_HANDLE_STATE(__HANDLE__) ((__HANDLE__)->State = HAL_COMP_STATE_RESET)

/**
  * @brief  Enable the specified comparator.
  * @param  __HANDLE__: COMP handle.
  * @retval None
  */
#define __HAL_COMP_ENABLE(__HANDLE__)                 (((__HANDLE__)->Instance == COMP1) ?    \
                                                       SET_BIT(COMP->CSR, COMP_CSR_COMP1EN) : \
                                                       SET_BIT(COMP->CSR, COMP_CSR_COMP2EN))
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

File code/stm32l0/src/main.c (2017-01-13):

/**
  ******************************************************************************
  * File Name          : main.c
  * Description        : Main program body
  ******************************************************************************
*/
/* Includes ------------------------------------------------------------------*/
#include "stm32l0xx_hal.h"
#include "user_funcs.h"

/* Private variables ---------------------------------------------------------*/
ADC_HandleTypeDef hadc;

TIM_HandleTypeDef htim2;
TIM_HandleTypeDef htim22;
DMA_HandleTypeDef hdma_tim2_ch1;
DMA_HandleTypeDef hdma_tim2_ch2;
DMA_HandleTypeDef hdma_tim2_ch3;
DMA_HandleTypeDef hdma_tim2_ch4;

/* Private variables ---------------------------------------------------------*/

/* Private function prototypes -----------------------------------------------*/
void SystemClock_Config(void);
static void MX_GPIO_Init(void);
static void MX_DMA_Init(void);
static void MX_ADC_Init(void);
static void MX_TIM2_Init(void);
static void MX_TIM22_Init(void);
void conv_init(batpins batx);

int main(void)
{

  /* MCU Configuration----------------------------------------------------------*/

  /* Reset of all peripherals, Initializes the Flash interface and the Systick. */
  HAL_Init();

  /* Configure the system clock */
  SystemClock_Config();

  /* Initialize all configured peripherals */
  MX_GPIO_Init();
  MX_DMA_Init();
  MX_ADC_Init();
  MX_TIM2_Init();
  MX_TIM22_Init();

  batpins battery3;
  batpins battery4;
  pwm_timers b3_tims;
  pwm_timers b4_tims;
  batprops props_bat3;
  batprops props_bat4;

  /* Battery 3 */
  b3_tims.conv_timer = htim2;
  b3_tims.dchg_timer = htim22;

  battery3.v_adc_chan = ADC_CHANNEL_4;
  battery3.i_adc_chan = ADC_CHANNEL_8;
  battery3.chg_port = chg_onoff_3_GPIO_Port;
  battery3.chg_pin = chg_onoff_3_Pin;
  battery3.dchg_pin = TIM_CHANNEL_1;
  battery3.conv_chg_pin = TIM_CHANNEL_1;
  battery3.conv_dchg_pin = TIM_CHANNEL_2;
  battery3.pwm_tims = b3_tims;

  props_bat3.i_adc_val = 0;
  props_bat3.v_adc_val = 0;
  props_bat3.adc_val_old = adc_read(battery3.i_adc_chan);
  props_bat3.id_adc_stpt = 993 + props_bat3.adc_val_old;
  props_bat3.ic_adc_stpt = props_bat3.adc_val_old - 993;
  props_bat3.conv_bst_stpt = 100; // Need to calibrate this to boost to desired voltage
  props_bat3.pwm_chg_stpt = 0; 	  // Initialized to 0. Program will change as needed.
  props_bat3.pwm_dchg_stpt = DCHG_PWM_INIT; // Initialize near where discharge FET turns on
  props_bat3.pi = 0;
  props_bat3.sw_ctr = 0;

  /* Battery 4 */
  b4_tims.conv_timer = htim2;
  b4_tims.dchg_timer = htim22;

  battery4.v_adc_chan = ADC_CHANNEL_11;
  battery4.i_adc_chan = ADC_CHANNEL_10;
  battery4.chg_port = chg_onoff_4_GPIO_Port;
  battery4.chg_pin = chg_onoff_4_Pin;
  battery4.dchg_pin = TIM_CHANNEL_2;
  battery4.conv_chg_pin = B4_CHG_CHAN; // Change in h file (used in multiple locations, dma_offset func)
  battery4.conv_dchg_pin = TIM_CHANNEL_4;
  battery4.pwm_tims = b4_tims;
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

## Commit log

2015-10-12 added kicad files
    [BatAger.kicad_pcb, BatAger.sch]
2015-10-12 modified: BatAger-cache.lib modified: BatAger.pro modified: BatAger.sch new file: lib/Gajda_amplif.lib
    [BatAger.sch]
2015-10-12 added directories
    [BatAger.kicad_pcb, BatAger.sch]
2015-10-12 new file: pcb/BatAger-cache.lib new file: pcb/BatAger.kicad_pcb new file: pcb/BatAger.pro new file: pcb/BatAger.sch new file: pcb/lib/Gajda_amplif.lib
    [BatAger.kicad_pcb, BatAger.sch]
2015-10-12 Added multiple schematic pages.
    [BatAger.sch, file561CB83A.sch, file561D4A90.sch]
2015-10-12 updated schematics
    [BatAger.sch, file561CB83A.sch, file561D4A90.sch, file561DD110.sch]
2015-10-13 starting on layout
    [BatAger.sch, file561CB83A.sch, file561D4A90.sch, file561DD110.sch]
2015-10-14 last commit before starting traces
    [BatAger.kicad_pcb, _saved_file561D4A90.sch, _saved_file561DD110.sch]
2015-10-14 trace complete (maybe!)
    [BatAger.kicad_pcb, BatAger.sch, _saved_file561D4A90.sch, _saved_file561DD110.sch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]
2015-10-14 done for today. i1 & i2 still unconnected.
    [BatAger.kicad_pcb]
2015-10-15 adding planes - almost done!
    [BatAger.kicad_pcb, BatAger.sch, file561DD110.sch]
2015-10-15 going to change drill sizes.
    [BatAger.kicad_pcb]
2015-10-15 Production candidate - passes DRC.
    [BatAger.kicad_pcb, BatAger.sch, file561CB83A.sch, file561D4A90.sch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]
2015-10-15 Reduced number of drill sizes.
    [BatAger-B_Cu.gbl, BatAger-Edge_Cuts.gm1, BatAger-F_Cu.gtl, BatAger-F_Fab.gbr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]
2015-10-16 Changed fan FET (Q22). Many other minor layout changes. Production candidate.
    [BatAger-B_Cu.gbl, BatAger-B_Mask.gbs, BatAger-B_Paste.gbp, BatAger-B_SilkS.gbo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]
2015-10-20 Added caps on discharge fet gates
    Need to filter the digital signal from the MCU to create an analog
    voltage at the gate because the fet should operate in between on and
    off states (which generates heat due to high Rds).
    [BatAger.kicad_pcb, BatAger.sch, file561CB83A.sch, file561D4A90.sch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]
2015-10-20 Changed R62 & C26 to PTH.
    [BatAger.kicad_pcb, BatAger.sch, file561CB83A.sch, file561D4A90.sch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]
2015-10-27 Minor package changes.
    [BatAger-B_Cu.gbl, BatAger-B_Mask.gbs, BatAger-B_Paste.gbp, BatAger-B_SilkS.gbo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]
2015-12-18 added stm32 code
2015-12-18 added example Arduino code that executes CC/CV charging
2016-01-12 pwm and adc fix
    Found that when using the ADC to set the pwm for the discharge pin, the PWM that controls the DC converter would start to emit irregular pulses. Maybe it has something to do with DMA. Ultimately I fo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
2016-01-15 added over current protection
    System is seeing significant noise issues. And while over-current protection works in tested scenarios, it failed at one point and fried the current sensor yet again. Pencils down - need to use previ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
2016-01-19 creating new branch
    For unknown reasons, the control is showing the same noise issues as last commit. Voltage can be increased >12V and current to at least 800mA without losing control.
2016-01-19 working on new dchg_ctrl function
    Also added several new data type to handle all the pins associated with one battery. Need to change the scope of the i32_pi_pwm_val variable since there will soon be many pwm values to track. Global 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
2016-01-22 new pi working well, need to make clean function
    the new pi loop uses a counter via interrupt to take an average reading that is greater than one EIS period, therefore the loop isn't trying to fight the sine wave of the EIS signal. Output is quite 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
2016-01-25 confirmed LVDC is working with bat
    Used voltage divider on the IV sensor for LV detection. Used power supply to bring below 10.5V to confirm load disconnects. Separately, also ran charging algo on bat and confirms works ok. On to char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
2016-03-10 can charge battery, but some issues
    Using a dummy load, the algorithm successfully transitions from CC to CV. When connected to an actual battery, it works in either CC or CV modes, but starts slamming between the two when trying to tr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
2016-03-15 improved PI loop
    less oscillation in loop at CC/CV transition, but current jumps when switching to CV. Need to reduce the buffer that prevents transition jumping
2016-03-18 Added plot files
    [BatAgerR1-B_Cu.gbl, BatAgerR1-B_Mask.gbs, BatAgerR1-B_Paste.gbp, BatAgerR1-B_SilkS.gbo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]
2016-04-07 switches modes properly
    charging works correctly, and switches ok to discharge. But during discharge it can trip off on high current. Appears that PI constants need to be tuned for discharging
2016-04-11 two battery channels tested
    Second channel outputs working ok. Going to try testing with power, but before doing will move battery definitions to dedicated header file.
2016-04-13 about to add libraries for STM32L0
2016-04-13 added libraries for stm32L0 :
2016-04-13 updated gitignore
    [BatAgerR1-B_Cu.gbl, BatAgerR1-B_Mask.gbs, BatAgerR1-B_Paste.gbp, BatAgerR1-B_SilkS.gbo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]
2016-04-13 stm32l0 code compiles and debugger launches and breaks properly
2016-04-19 major problems with timing on stm32l0
    not sure why it cropped up during of testing of 2nd battery with L0, since testing with first battery went fine.
2016-04-25 discharge ok, working on charging
    tested one battery discharging with multi-channel code, and while it is working, timing again seems to be an issue. The current jumping up and down. Began work on charging, but in the middle of debug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
2016-07-19 PI loop working in chg and dchg
    but in chg mode over current trips before settling down to be ok. Also connected battery to do discharge test and blown fuse. Not sure why
2016-07-20 acquired replacement F0 brd (all are now L0), updating pins
    Changing pins on board 1 to match the configuration of the F0 (don't want to re-solder all the pins to match the L0 config of boards 2/3). Requires substantial ifdef's
2016-07-28 bat2 full test successful
    used 11.45V LVDC, 12V CV stpts. Properly switched from discharge -> CC -> CV
2016-10-28 updated so each bat has its own current origin
2017-01-13 about to muck with PI gains
    gains seem fine until dchg reaches ~11.5V, after which it oscillates wwildly, preventing the dchg cycle from finishing smoothly

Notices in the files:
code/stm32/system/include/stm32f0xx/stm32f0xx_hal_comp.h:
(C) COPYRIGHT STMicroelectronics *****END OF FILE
